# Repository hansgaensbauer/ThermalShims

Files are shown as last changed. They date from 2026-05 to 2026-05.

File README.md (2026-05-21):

# Thermal Shims

## Shim Demos

### Concentric Rings

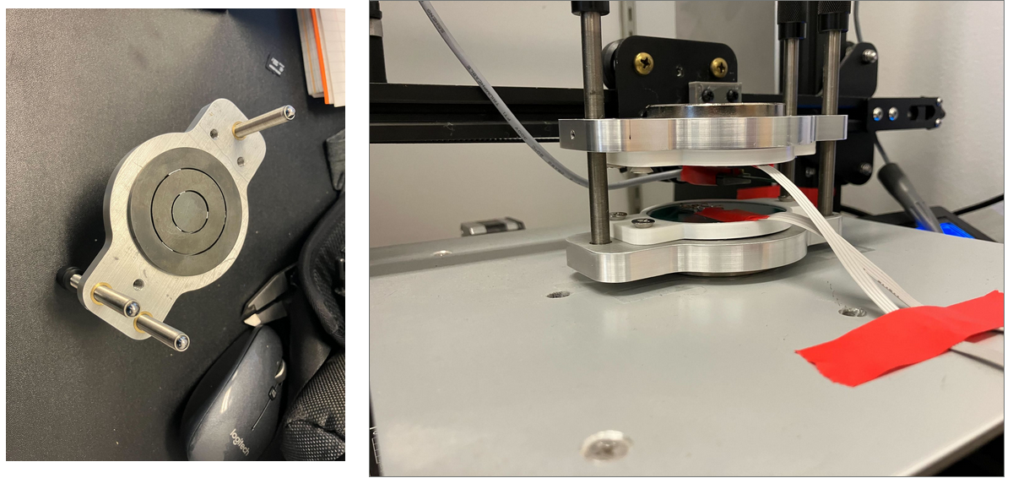
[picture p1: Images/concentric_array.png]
Concentric Ring Demo


This demonstration uses a 4mm ferrite plate cut to size on a waterjet. Each ring is connected to a PCB heater that is counterwound to prevent the development of magnetic fields from the heater current.

### 12x12 Array

This board demonstrates independent closed-loop control over the temperature of 144 ferrite elements. Each ferrite element has a temperature control unit cell attached on the backside of the PCB. This circuit uses two dual-MOSFETs to provide DRAM-like array access to the power setting and temperature readout for that element:

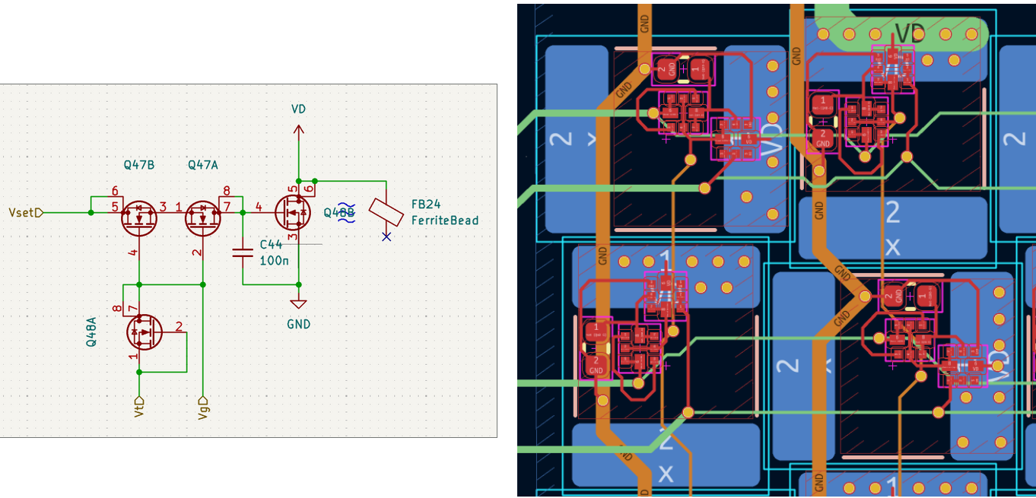
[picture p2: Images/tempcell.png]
A temperature control unit cell schematic and layout


These unit cells can then be connected to form a larger array of N elements, with only sqrt(N) control circuits/ADCs required:

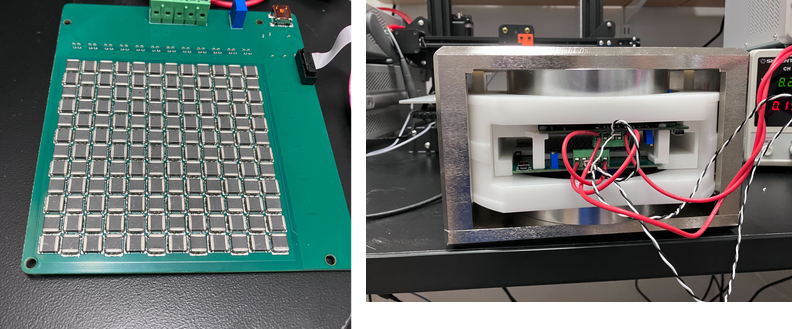
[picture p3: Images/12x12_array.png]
The shim arrays installed in a permanent magnet

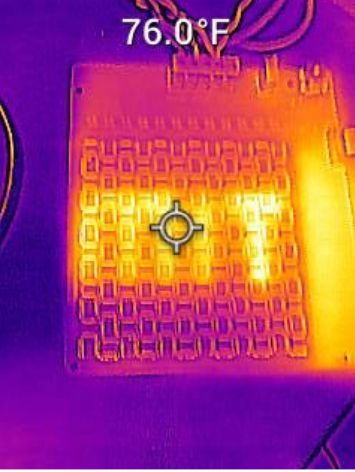
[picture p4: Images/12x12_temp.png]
A demonstration of the independent temperature control


The `12x12 Array` folder contains simulations of the control circuits showing the sequencing required to measure the temperature or set the cell power level. All of this circuitry is included on the PCB for the 12x12 array demo.

### Hub & Spoke NdFeB Magnet Shimming

This board provides temperature control and sensing for 32 NdFeB magnets in a hub & spoke magnet array. This can be used to prevent temperature drift between the magnets during a scan, or even to account for variations in the magnetization of the individual elements. 

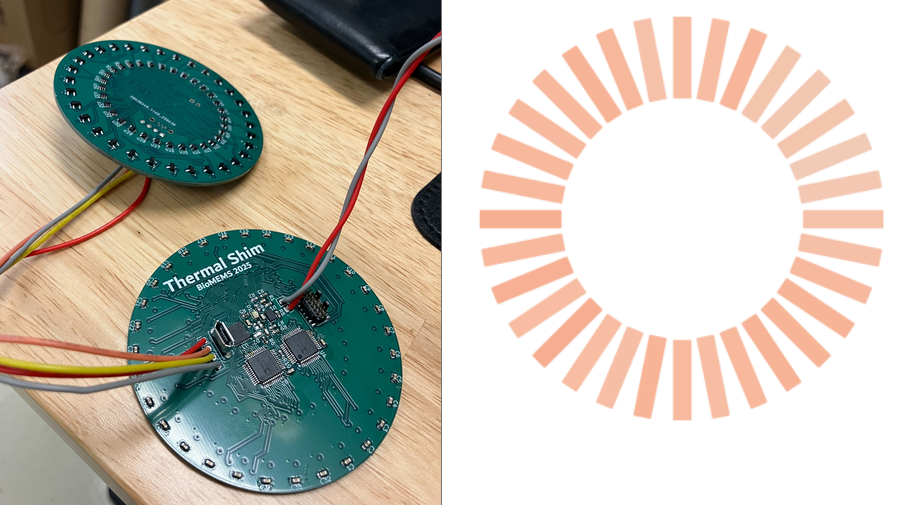
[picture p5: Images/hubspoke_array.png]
Hub and spoke magnet temperature control


## Simulations
The jupyter notebook in the Simulations folder includes code for simulating different arrangements of thermal shims with different temperatures using [FEMM](https://www.femm.info/). These simulations assume an arctangent B/H curve that is parameterized by a linear relationship between the saturation magnetization and the temperature:

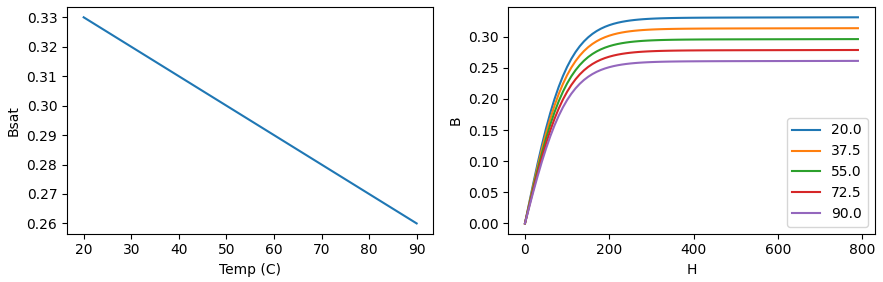
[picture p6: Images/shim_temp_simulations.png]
BH Curve simulations


To run a simulation with a certain material and temperature, the code creates a custom material based on the calculated BH curve in FEMM. To sweep the temperature, the same simulation is run with different materials.

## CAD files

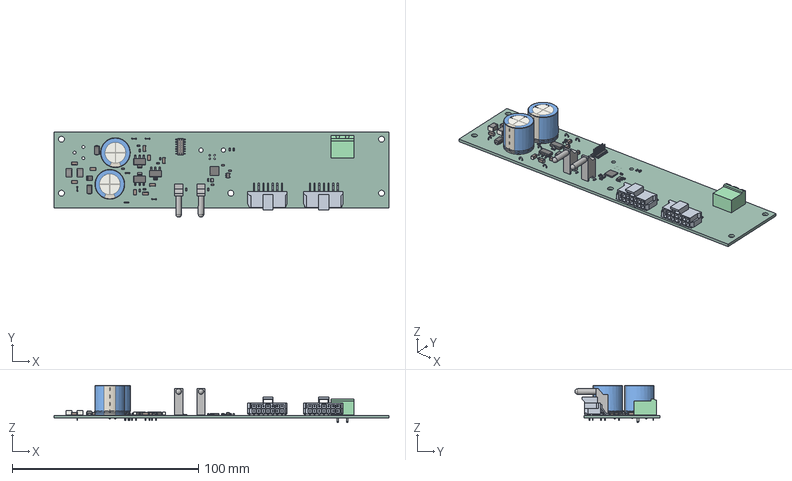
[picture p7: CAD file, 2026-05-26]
Flow Shims/hardware/controller/controller.step
180.0 x 45.9 x 20.0 mm
C_1206_3216Metric x 9
CP_Radial_D16.0mm_P7.50mm x 2
TestPoint_Bridge_Pitch2.0mm_Drill0.7mm x 6
SLP3-500-450-R x 2
C_0603_1608Metric x 5
L_1812_4532Metric x 2
R_0603_1608Metric x 10
D_SMA x 2
Crystal_SMD_2016-4Pin_2.0x1.6mm
LED_0603_1608Metric x 2
SOT-223 x 3
Fuse_1210_3225Metric
SOT-23-5
QFN-32-1EP_5x5mm_P0.5mm_EP3.45x3.45mm
PinHeader_2x07_P1.27mm_Vertical_SMD
PhoenixContact_MSTBA_2,5_2-G-5,08_1x02_P5.08mm_Horizontal
controller_PCB

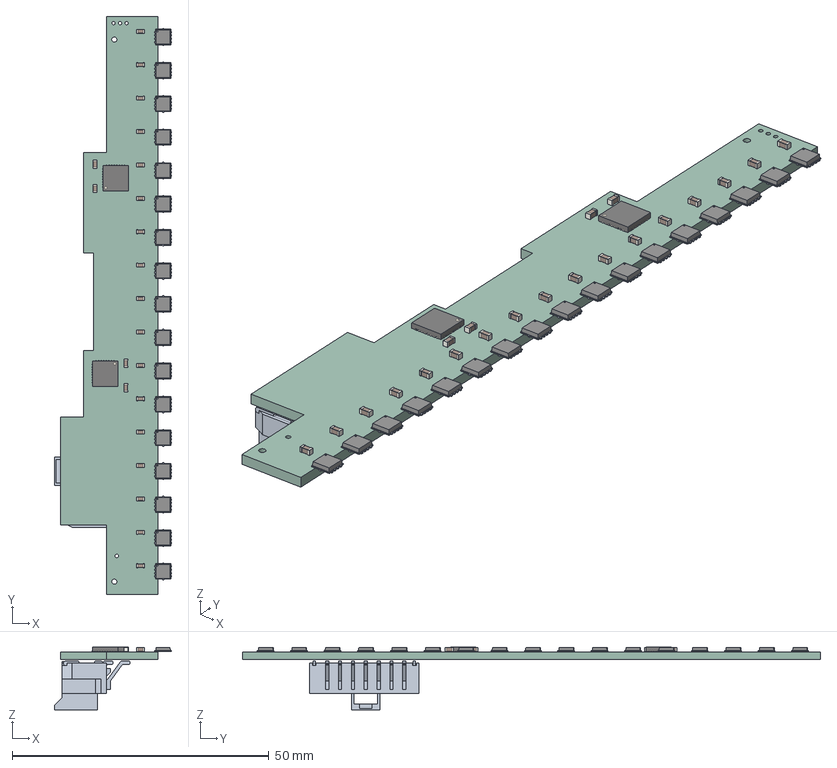
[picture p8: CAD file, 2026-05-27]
Flow Shims/hardware/heater17/heater17.step
22.8 x 112.5 x 12.3 mm
C_0603_1608Metric x 21
QFN-32-1EP_5x5mm_P0.5mm_EP3.3x3.3mm x 2
NVTFS5116PLTAG x 17
heater_PCB

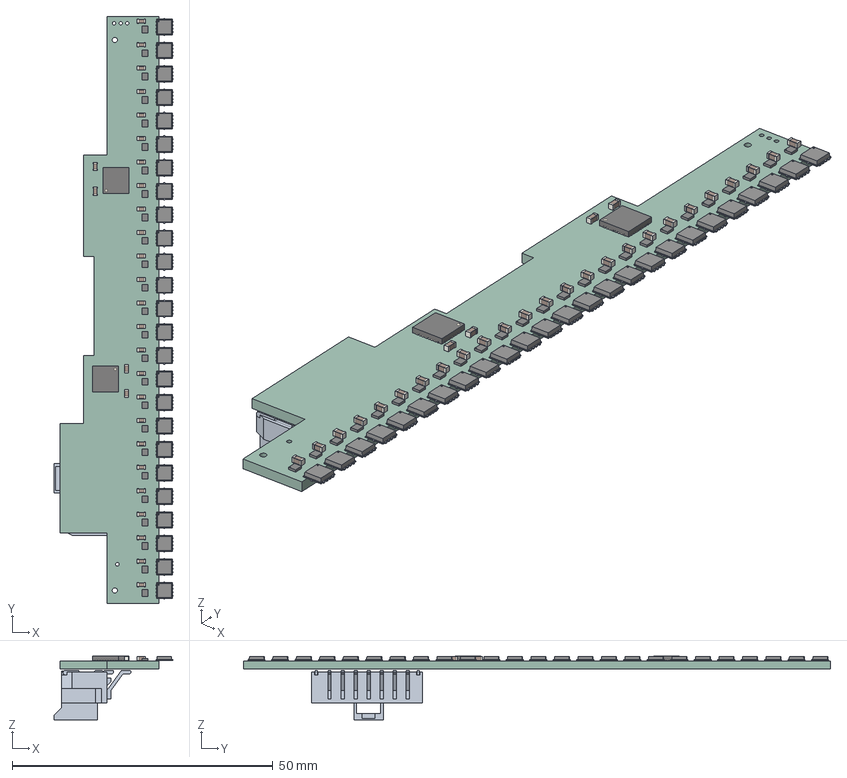
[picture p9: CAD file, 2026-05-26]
Flow Shims/hardware/heater25/heater.step
22.8 x 112.5 x 12.3 mm
NVTFS5116PLTAG x 25
C_0603_1608Metric x 29
QFN-32-1EP_5x5mm_P0.5mm_EP3.3x3.3mm x 2
DFN6_1_2X1_3_STM x 25
heater_PCB

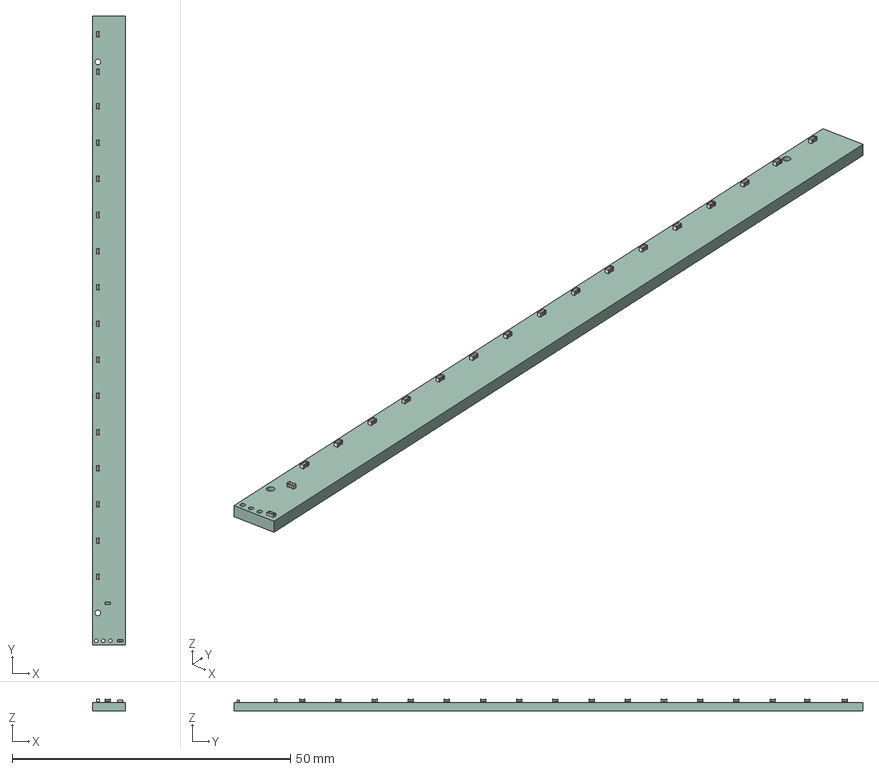
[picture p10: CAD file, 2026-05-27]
Flow Shims/hardware/temp_sensors17/temp_sensor17.step
6.00 x 113.0 x 2.09 mm
C_0402_1005Metric x 17
R_0402_1005Metric
temp_sensors_PCB

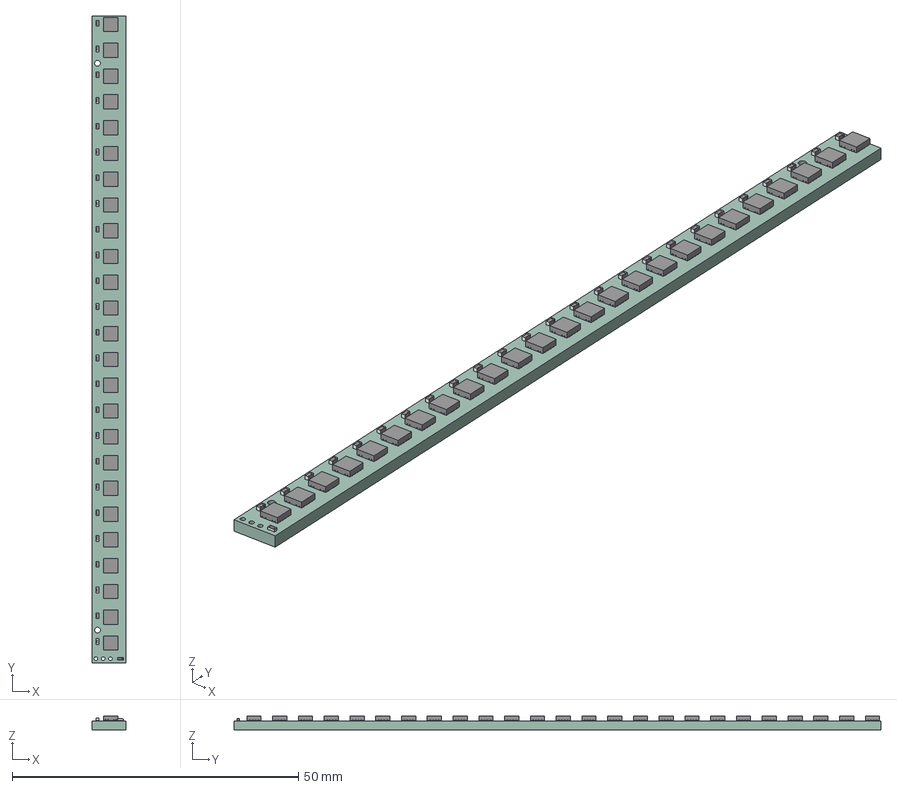
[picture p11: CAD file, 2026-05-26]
Flow Shims/hardware/temp_sensors25/temp_sensor.step
6.00 x 113.0 x 2.40 mm
C_0402_1005Metric x 25
BODY-SON x 25
FRAME-NGR0008C x 25
PIN1-ID x 25
R_0402_1005Metric
temp_sensors_PCB

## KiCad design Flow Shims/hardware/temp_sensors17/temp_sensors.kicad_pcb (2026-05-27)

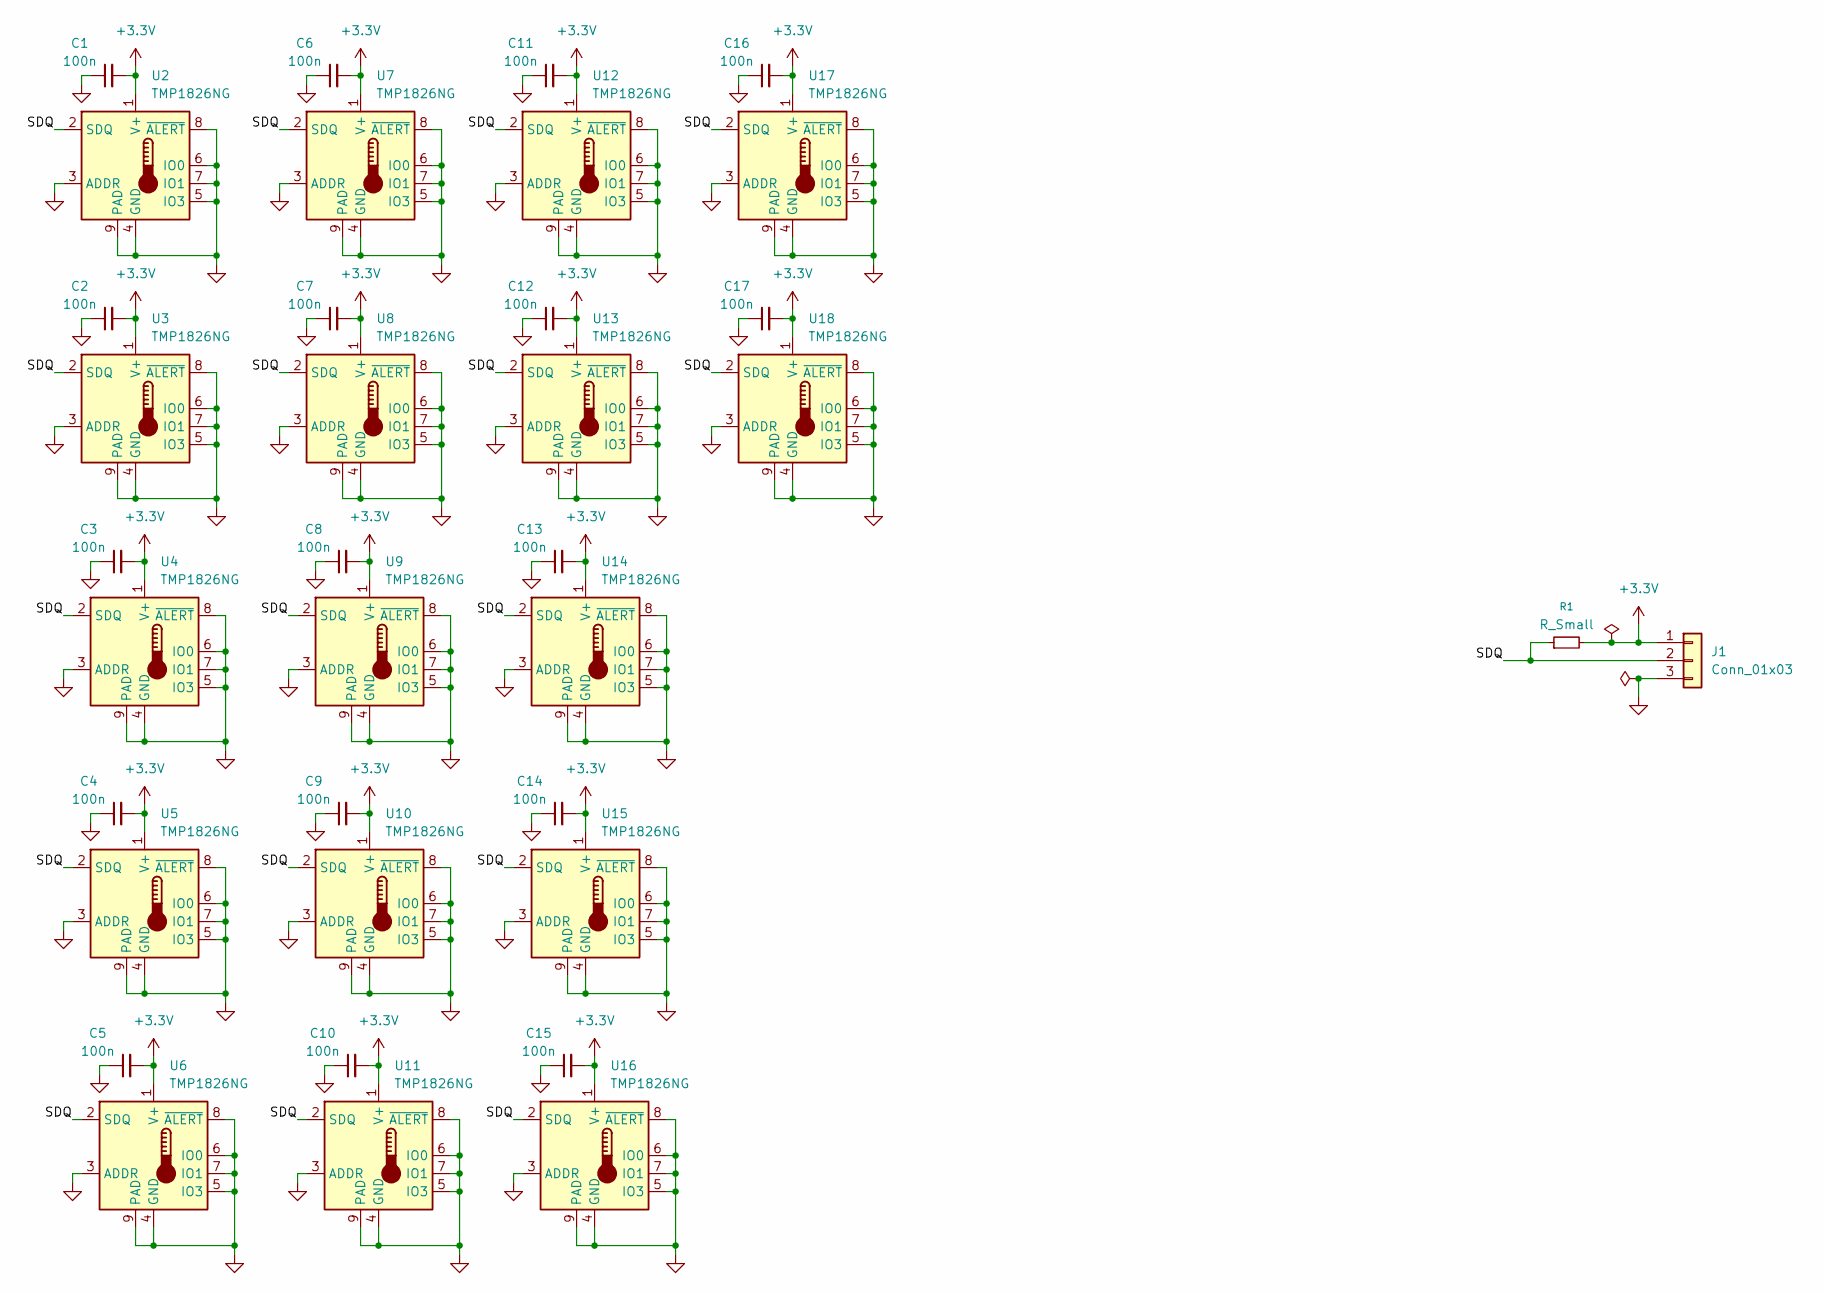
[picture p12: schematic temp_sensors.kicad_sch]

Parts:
C1, C2, C3, C4, C5, C6, C7, C8, C9, C10, C11, C12, C13, C14, C15, C16, C17: 100n; C_0402_1005Metric
J1: Conn_01x03; PinHeader_1x03_P1.27mm_Vertical
R1: R_Small; R_0402_1005Metric
U2, U3, U4, U5, U6, U7, U8, U9, U10, U11, U12, U13, U14, U15, U16, U17, U18: TMP1826NG; Sensirion_DFN-8-1EP_2.5x2.5mm_P0.5mm_EP1.1x1.7mm

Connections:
+3.3V: C1.2, C2.2, C3.2, C4.2, C5.2, C6.2, C7.2, C8.2, C9.2, C10.2, C11.2, C12.2, C13.2, C14.2, C15.2, C16.2, C17.2, J1.1, R1.2, U2.1 (V+), U3.1 (V+), U4.1 (V+), U5.1 (V+), U6.1 (V+), U7.1 (V+), U8.1 (V+), U9.1 (V+), U10.1 (V+), U11.1 (V+), U12.1 (V+), U13.1 (V+), U14.1 (V+), U15.1 (V+), U16.1 (V+), U17.1 (V+), U18.1 (V+)
/SDQ: J1.2, R1.1, U2.2 (SDQ), U3.2 (SDQ), U4.2 (SDQ), U5.2 (SDQ), U6.2 (SDQ), U7.2 (SDQ), U8.2 (SDQ), U9.2 (SDQ), U10.2 (SDQ), U11.2 (SDQ), U12.2 (SDQ), U13.2 (SDQ), U14.2 (SDQ), U15.2 (SDQ), U16.2 (SDQ), U17.2 (SDQ), U18.2 (SDQ)
GND: C1.1, C2.1, C3.1, C4.1, C5.1, C6.1, C7.1, C8.1, C9.1, C10.1, C11.1, C12.1, C13.1, C14.1, C15.1, C16.1, C17.1, J1.3, U2.3 (ADDR), U2.4 (GND), U2.5 (IO3), U2.6 (IO0), U2.7 (IO1), U2.8 (~ALERT), U2.9 (PAD), U3.3 (ADDR), U3.4 (GND), U3.5 (IO3), U3.6 (IO0), U3.7 (IO1), U3.8 (~ALERT), U3.9 (PAD), U4.3 (ADDR), U4.4 (GND), U4.5 (IO3), U4.6 (IO0), U4.7 (IO1), U4.8 (~ALERT), U4.9 (PAD), U5.3 (ADDR), U5.4 (GND), U5.5 (IO3), U5.6 (IO0), U5.7 (IO1), U5.8 (~ALERT), U5.9 (PAD), U6.3 (ADDR), U6.4 (GND), U6.5 (IO3), U6.6 (IO0), U6.7 (IO1), U6.8 (~ALERT), U6.9 (PAD), U7.3 (ADDR), U7.4 (GND), U7.5 (IO3), U7.6 (IO0), U7.7 (IO1), U7.8 (~ALERT), U7.9 (PAD), U8.3 (ADDR), U8.4 (GND), U8.5 (IO3), U8.6 (IO0), U8.7 (IO1), U8.8 (~ALERT), U8.9 (PAD), U9.3 (ADDR), U9.4 (GND), U9.5 (IO3), U9.6 (IO0), U9.7 (IO1), U9.8 (~ALERT), U9.9 (PAD), U10.3 (ADDR), U10.4 (GND), U10.5 (IO3), U10.6 (IO0), U10.7 (IO1), U10.8 (~ALERT), U10.9 (PAD), U11.3 (ADDR), U11.4 (GND), U11.5 (IO3), U11.6 (IO0), U11.7 (IO1), U11.8 (~ALERT), U11.9 (PAD), U12.3 (ADDR), U12.4 (GND), U12.5 (IO3), U12.6 (IO0), U12.7 (IO1), U12.8 (~ALERT), U12.9 (PAD), U13.3 (ADDR), U13.4 (GND), U13.5 (IO3), U13.6 (IO0), U13.7 (IO1), U13.8 (~ALERT), U13.9 (PAD), U14.3 (ADDR), U14.4 (GND), U14.5 (IO3), U14.6 (IO0), U14.7 (IO1), U14.8 (~ALERT), U14.9 (PAD), U15.3 (ADDR), U15.4 (GND), U15.5 (IO3), U15.6 (IO0), U15.7 (IO1), U15.8 (~ALERT), U15.9 (PAD), U16.3 (ADDR), U16.4 (GND), U16.5 (IO3), U16.6 (IO0), U16.7 (IO1), U16.8 (~ALERT), U16.9 (PAD), U17.3 (ADDR), U17.4 (GND), U17.5 (IO3), U17.6 (IO0), U17.7 (IO1), U17.8 (~ALERT), U17.9 (PAD), U18.3 (ADDR), U18.4 (GND), U18.5 (IO3), U18.6 (IO0), U18.7 (IO1), U18.8 (~ALERT), U18.9 (PAD)

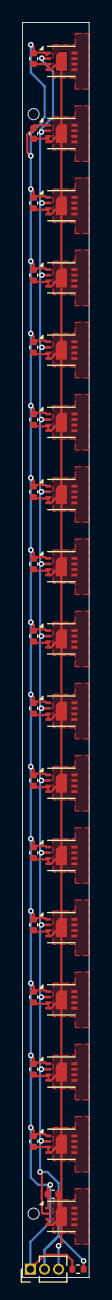
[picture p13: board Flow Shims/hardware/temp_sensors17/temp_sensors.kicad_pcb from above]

Board: 2 copper layers, 6.0 x 113.0 mm, 36 parts (0 on the bottom side), 3 nets.

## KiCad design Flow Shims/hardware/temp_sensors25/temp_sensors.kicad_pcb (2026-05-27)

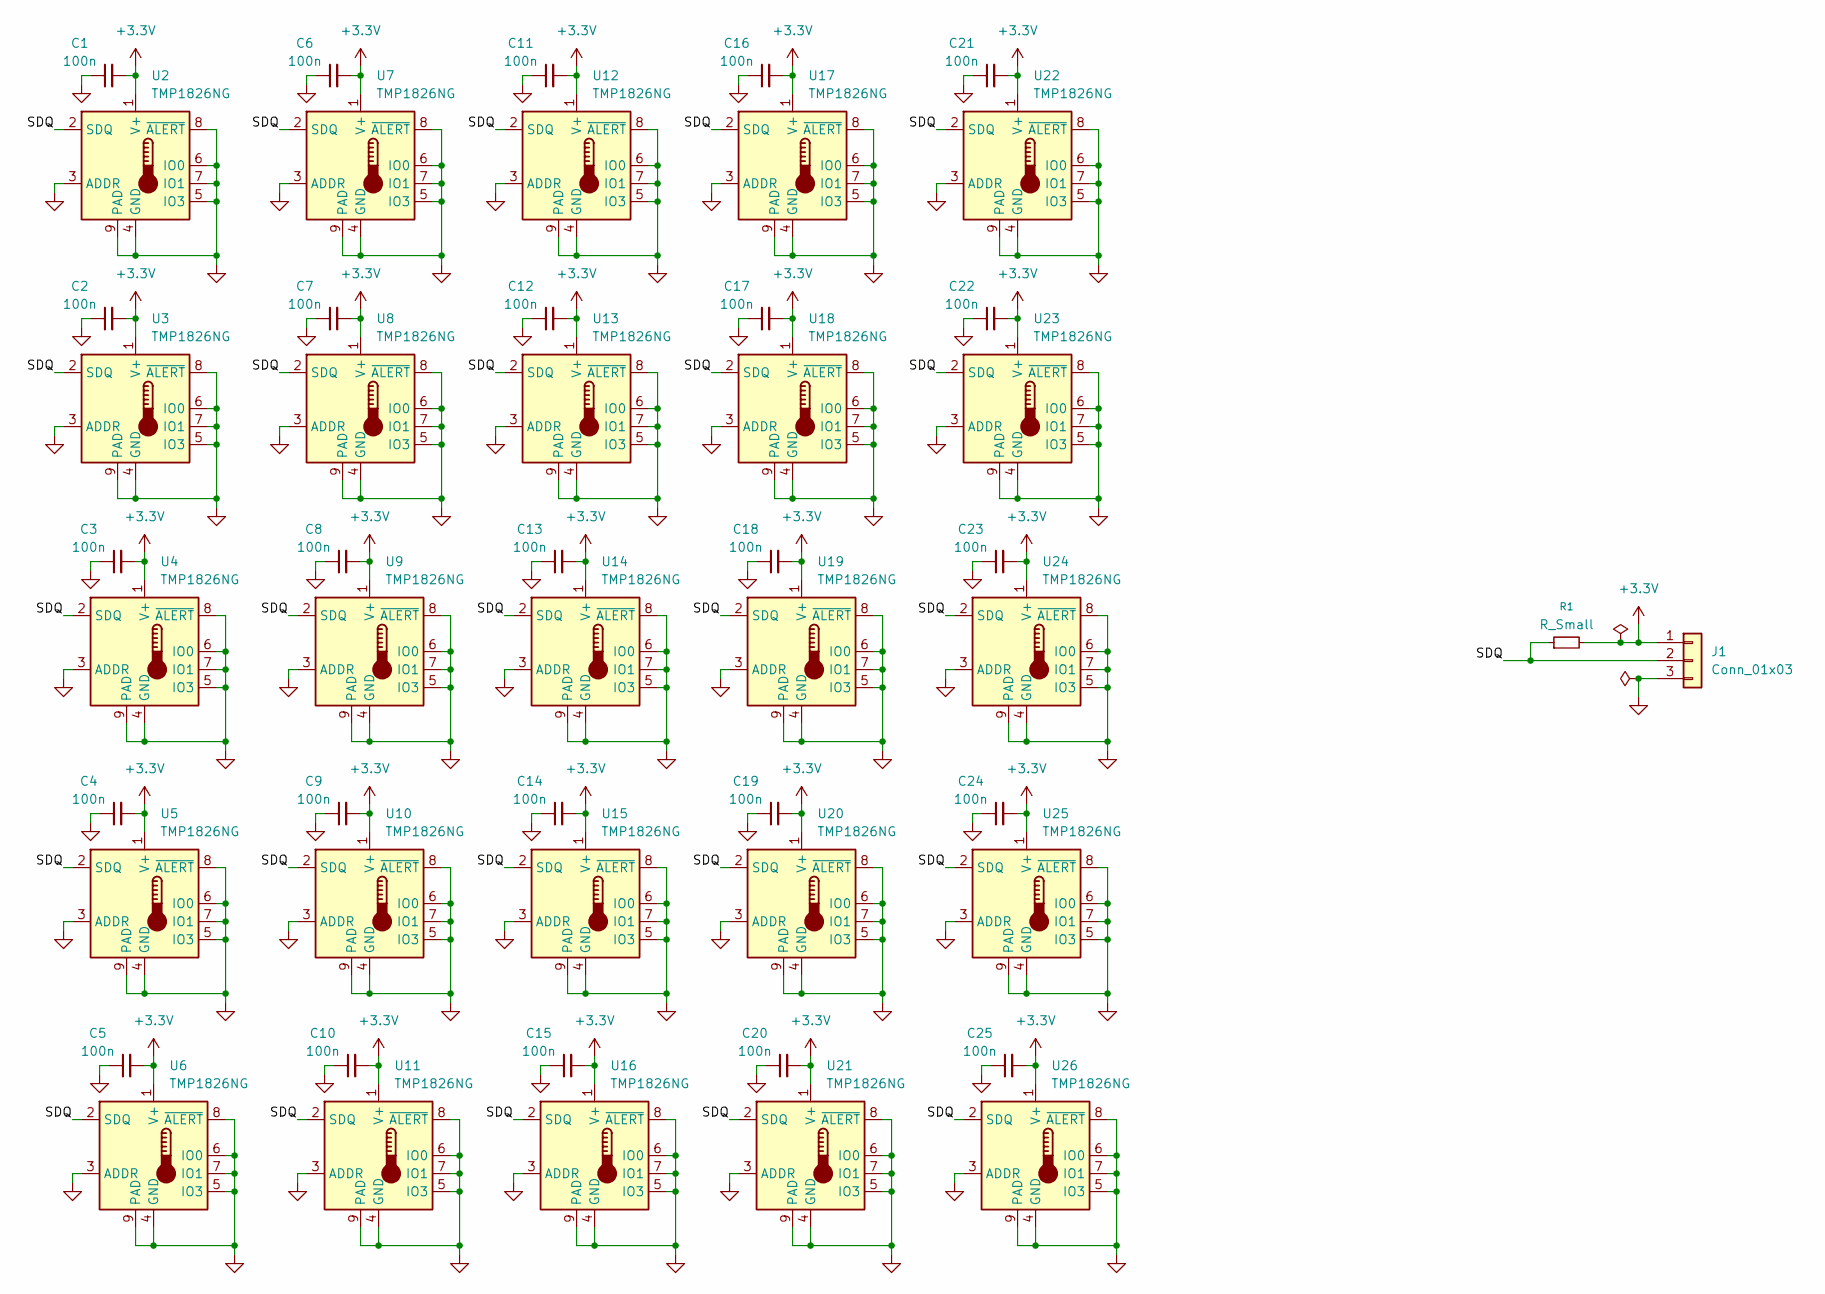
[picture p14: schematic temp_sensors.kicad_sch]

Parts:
C1, C2, C3, C4, C5, C6, C7, C8, C9, C10, C11, C12, C13, C14, C15, C16, C17, C18, C19, C20, C21, C22, C23, C24, C25: 100n; C_0402_1005Metric
J1: Conn_01x03; PinHeader_1x03_P1.27mm_Vertical
R1: R_Small; R_0402_1005Metric
U2, U3, U4, U5, U6, U7, U8, U9, U10, U11, U12, U13, U14, U15, U16, U17, U18, U19, U20, U21, U22, U23, U24, U25, U26: TMP1826NG; Sensirion_DFN-8-1EP_2.5x2.5mm_P0.5mm_EP1.1x1.7mm

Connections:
+3.3V: C1.2, C2.2, C3.2, C4.2, C5.2, C6.2, C7.2, C8.2, C9.2, C10.2, C11.2, C12.2, C13.2, C14.2, C15.2, C16.2, C17.2, C18.2, C19.2, C20.2, C21.2, C22.2, C23.2, C24.2, C25.2, J1.1, R1.2, U2.1 (V+), U3.1 (V+), U4.1 (V+), U5.1 (V+), U6.1 (V+), U7.1 (V+), U8.1 (V+), U9.1 (V+), U10.1 (V+), U11.1 (V+), U12.1 (V+), U13.1 (V+), U14.1 (V+), U15.1 (V+), U16.1 (V+), U17.1 (V+), U18.1 (V+), U19.1 (V+), U20.1 (V+), U21.1 (V+), U22.1 (V+), U23.1 (V+), U24.1 (V+), U25.1 (V+), U26.1 (V+)
/SDQ: J1.2, R1.1, U2.2 (SDQ), U3.2 (SDQ), U4.2 (SDQ), U5.2 (SDQ), U6.2 (SDQ), U7.2 (SDQ), U8.2 (SDQ), U9.2 (SDQ), U10.2 (SDQ), U11.2 (SDQ), U12.2 (SDQ), U13.2 (SDQ), U14.2 (SDQ), U15.2 (SDQ), U16.2 (SDQ), U17.2 (SDQ), U18.2 (SDQ), U19.2 (SDQ), U20.2 (SDQ), U21.2 (SDQ), U22.2 (SDQ), U23.2 (SDQ), U24.2 (SDQ), U25.2 (SDQ), U26.2 (SDQ)
GND: C1.1, C2.1, C3.1, C4.1, C5.1, C6.1, C7.1, C8.1, C9.1, C10.1, C11.1, C12.1, C13.1, C14.1, C15.1, C16.1, C17.1, C18.1, C19.1, C20.1, C21.1, C22.1, C23.1, C24.1, C25.1, J1.3, U2.3 (ADDR), U2.4 (GND), U2.5 (IO3), U2.6 (IO0), U2.7 (IO1), U2.8 (~ALERT), U2.9 (PAD), U3.3 (ADDR), U3.4 (GND), U3.5 (IO3), U3.6 (IO0), U3.7 (IO1), U3.8 (~ALERT), U3.9 (PAD), U4.3 (ADDR), U4.4 (GND), U4.5 (IO3), U4.6 (IO0), U4.7 (IO1), U4.8 (~ALERT), U4.9 (PAD), U5.3 (ADDR), U5.4 (GND), U5.5 (IO3), U5.6 (IO0), U5.7 (IO1), U5.8 (~ALERT), U5.9 (PAD), U6.3 (ADDR), U6.4 (GND), U6.5 (IO3), U6.6 (IO0), U6.7 (IO1), U6.8 (~ALERT), U6.9 (PAD), U7.3 (ADDR), U7.4 (GND), U7.5 (IO3), U7.6 (IO0), U7.7 (IO1), U7.8 (~ALERT), U7.9 (PAD), U8.3 (ADDR), U8.4 (GND), U8.5 (IO3), U8.6 (IO0), U8.7 (IO1), U8.8 (~ALERT), U8.9 (PAD), U9.3 (ADDR), U9.4 (GND), U9.5 (IO3), U9.6 (IO0), U9.7 (IO1), U9.8 (~ALERT), U9.9 (PAD), U10.3 (ADDR), U10.4 (GND), U10.5 (IO3), U10.6 (IO0), U10.7 (IO1), U10.8 (~ALERT), U10.9 (PAD), U11.3 (ADDR), U11.4 (GND), U11.5 (IO3), U11.6 (IO0), U11.7 (IO1), U11.8 (~ALERT), U11.9 (PAD), U12.3 (ADDR), U12.4 (GND), U12.5 (IO3), U12.6 (IO0), U12.7 (IO1), U12.8 (~ALERT), U12.9 (PAD), U13.3 (ADDR), U13.4 (GND), U13.5 (IO3), U13.6 (IO0), U13.7 (IO1), U13.8 (~ALERT), U13.9 (PAD), U14.3 (ADDR), U14.4 (GND), U14.5 (IO3), U14.6 (IO0), U14.7 (IO1), U14.8 (~ALERT), U14.9 (PAD), U15.3 (ADDR), U15.4 (GND), U15.5 (IO3), U15.6 (IO0), U15.7 (IO1), U15.8 (~ALERT), U15.9 (PAD), U16.3 (ADDR), U16.4 (GND), U16.5 (IO3), U16.6 (IO0), U16.7 (IO1), U16.8 (~ALERT), U16.9 (PAD), U17.3 (ADDR), U17.4 (GND), U17.5 (IO3), U17.6 (IO0), U17.7 (IO1), U17.8 (~ALERT), U17.9 (PAD), U18.3 (ADDR), U18.4 (GND), U18.5 (IO3), U18.6 (IO0), U18.7 (IO1), U18.8 (~ALERT), U18.9 (PAD), U19.3 (ADDR), U19.4 (GND), U19.5 (IO3), U19.6 (IO0), U19.7 (IO1), U19.8 (~ALERT), U19.9 (PAD), U20.3 (ADDR), U20.4 (GND), U20.5 (IO3), U20.6 (IO0), U20.7 (IO1), U20.8 (~ALERT), U20.9 (PAD), U21.3 (ADDR), U21.4 (GND), U21.5 (IO3), U21.6 (IO0), U21.7 (IO1), U21.8 (~ALERT), U21.9 (PAD), U22.3 (ADDR), U22.4 (GND), U22.5 (IO3), U22.6 (IO0), U22.7 (IO1), U22.8 (~ALERT), U22.9 (PAD), U23.3 (ADDR), U23.4 (GND), U23.5 (IO3), U23.6 (IO0), U23.7 (IO1), U23.8 (~ALERT), U23.9 (PAD), U24.3 (ADDR), U24.4 (GND), U24.5 (IO3), U24.6 (IO0), U24.7 (IO1), U24.8 (~ALERT), U24.9 (PAD), U25.3 (ADDR), U25.4 (GND), U25.5 (IO3), U25.6 (IO0), U25.7 (IO1), U25.8 (~ALERT), U25.9 (PAD), U26.3 (ADDR), U26.4 (GND), U26.5 (IO3), U26.6 (IO0), U26.7 (IO1), U26.8 (~ALERT), U26.9 (PAD)

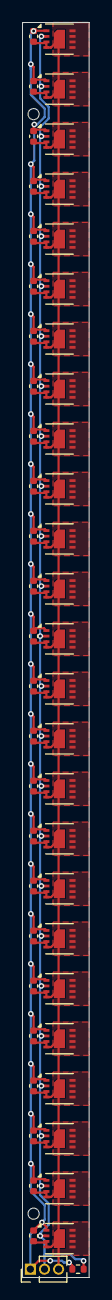
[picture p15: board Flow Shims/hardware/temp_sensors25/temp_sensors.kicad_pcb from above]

Board: 2 copper layers, 6.0 x 113.0 mm, 52 parts (0 on the bottom side), 3 nets.

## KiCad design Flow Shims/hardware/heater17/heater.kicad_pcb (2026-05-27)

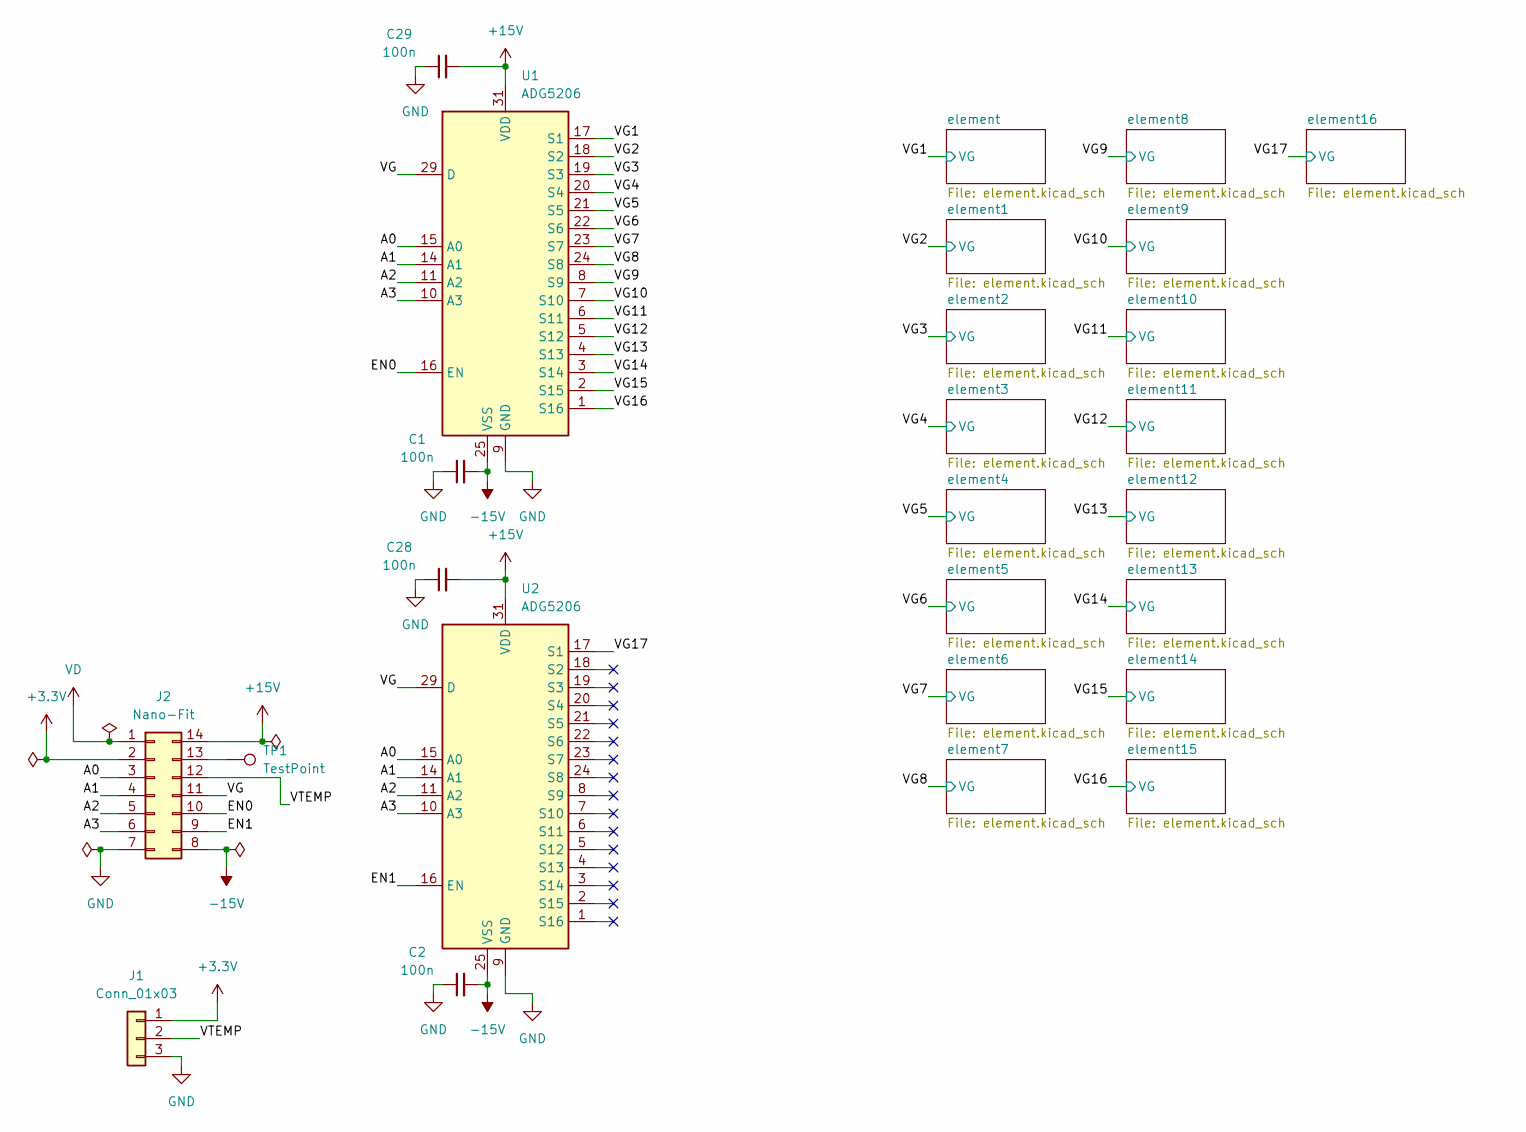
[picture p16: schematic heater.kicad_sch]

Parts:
C1, C2, C28, C29: 100n; C_0603_1608Metric
J1: Conn_01x03; PinHeader_1x03_P1.27mm_Vertical
J2: Nano-Fit; CONN_SD-105405-001_14_MOL
TP1: TestPoint; TestPoint_THTPad_D1.5mm_Drill0.7mm
U1, U2: ADG5206; QFN-32-1EP_5x5mm_P0.5mm_EP3.6x3.6mm

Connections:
+3.3V: J1.1, J2.2; also elsewhere on the board
+15V: C28.2, C29.2, J2.14, U1.31 (VDD), U2.31 (VDD)
-15V: C1.2, C2.2, J2.8, U1.25 (VSS), U1.33 (PAD), U2.25 (VSS), U2.33 (PAD)
/A0: J2.3, U1.15 (A0), U2.15 (A0)
/A1: J2.4, U1.14 (A1), U2.14 (A1)
/A2: J2.5, U1.11 (A2), U2.11 (A2)
/A3: J2.6, U1.10 (A3), U2.10 (A3)
/EN0: J2.10, U1.16 (EN)
/EN1: J2.9, U2.16 (EN)
/VG: J2.11, U1.29 (D), U2.29 (D)
/VG1: U1.17 (S1); also elsewhere on the board
/VG2: U1.18 (S2); also elsewhere on the board
/VG3: U1.19 (S3); also elsewhere on the board
/VG4: U1.20 (S4); also elsewhere on the board
/VG5: U1.21 (S5); also elsewhere on the board
/VG6: U1.22 (S6); also elsewhere on the board
/VG7: U1.23 (S7); also elsewhere on the board
/VG8: U1.24 (S8); also elsewhere on the board
/VG9: U1.8 (S9); also elsewhere on the board
/VG10: U1.7 (S10); also elsewhere on the board
/VG11: U1.6 (S11); also elsewhere on the board
/VG12: U1.5 (S12); also elsewhere on the board
/VG13: U1.4 (S13); also elsewhere on the board
/VG14: U1.3 (S14); also elsewhere on the board
/VG15: U1.2 (S15); also elsewhere on the board
/VG16: U1.1 (S16); also elsewhere on the board
/VG17: U2.17 (S1); also elsewhere on the board
/VTEMP: J1.2, J2.12
GND: C1.1, C2.1, C28.1, C29.1, J1.3, J2.7, U1.9 (GND), U2.9 (GND); also elsewhere on the board
unnamed: J2.13, TP1.1 (1_1)
VD: J2.1; also elsewhere on the board

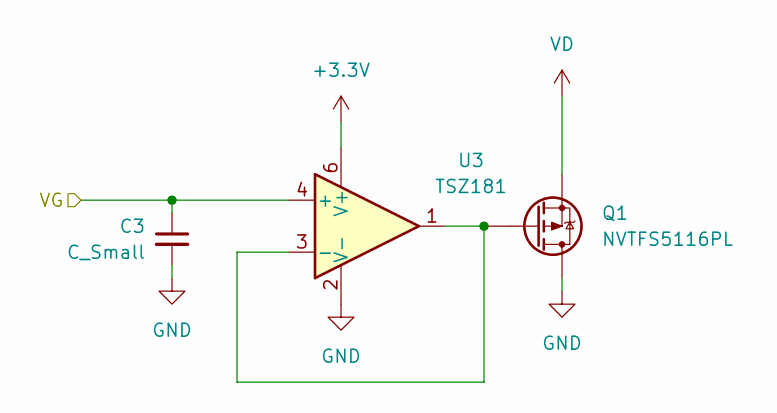
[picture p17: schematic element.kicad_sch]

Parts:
C3: C_Small; C_0603_1608Metric
Q1: NVTFS5116PL; WDFN8_511AB_ONS_OSI
U3: TSZ181; DFN-6_1.3x1.2mm_P0.4mm

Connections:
+3.3V: U3.6 (V+); also elsewhere on the board
/VG1: C3.1, U3.4 (+); also elsewhere on the board
GND: C3.2, Q1.5, Q1.6, Q1.7, Q1.8, U3.2 (V-); also elsewhere on the board
unnamed: Q1.4, U3.1, U3.3 (-)
VD: Q1.1, Q1.2, Q1.3; also elsewhere on the board

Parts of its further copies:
C4, C5, C6, C7, C8, C9, C10, C11, C12, C13, C14, C15, C16, C17, C18, C19: C_Small; C_0603_1608Metric
Q2, Q3, Q4, Q5, Q6, Q7, Q8, Q9, Q10, Q11, Q12, Q13, Q14, Q15, Q16, Q17: NVTFS5116PL; WDFN8_511AB_ONS_OSI
U4, U5, U6, U7, U8, U9, U10, U11, U12, U13, U14, U15, U16, U17, U18, U19: TSZ181; DFN-6_1.3x1.2mm_P0.4mm

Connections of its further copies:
+3.3V: U4.6 (V+), U5.6 (V+), U6.6 (V+), U7.6 (V+), U8.6 (V+), U9.6 (V+), U10.6 (V+), U11.6 (V+), U12.6 (V+), U13.6 (V+), U14.6 (V+), U15.6 (V+), U16.6 (V+), U17.6 (V+), U18.6 (V+), U19.6 (V+); also elsewhere on the board
/VG2: C4.1, U4.4 (+); also elsewhere on the board
/VG3: C5.1, U5.4 (+); also elsewhere on the board
/VG4: C6.1, U6.4 (+); also elsewhere on the board
/VG5: C7.1, U7.4 (+); also elsewhere on the board
/VG6: C8.1, U8.4 (+); also elsewhere on the board
/VG7: C9.1, U9.4 (+); also elsewhere on the board
/VG8: C10.1, U10.4 (+); also elsewhere on the board
/VG9: C11.1, U11.4 (+); also elsewhere on the board
/VG10: C12.1, U12.4 (+); also elsewhere on the board
/VG11: C13.1, U13.4 (+); also elsewhere on the board
/VG12: C14.1, U14.4 (+); also elsewhere on the board
/VG13: C15.1, U15.4 (+); also elsewhere on the board
/VG14: C16.1, U16.4 (+); also elsewhere on the board
/VG15: C17.1, U17.4 (+); also elsewhere on the board
/VG16: C18.1, U18.4 (+); also elsewhere on the board
/VG17: C19.1, U19.4 (+); also elsewhere on the board
GND: C4.2, C5.2, C6.2, C7.2, C8.2, C9.2, C10.2, C11.2, C12.2, C13.2, C14.2, C15.2, C16.2, C17.2, C18.2, C19.2, Q2.5, Q2.6, Q2.7, Q2.8, Q3.5, Q3.6, Q3.7, Q3.8, Q4.5, Q4.6, Q4.7, Q4.8, Q5.5, Q5.6, Q5.7, Q5.8, Q6.5, Q6.6, Q6.7, Q6.8, Q7.5, Q7.6, Q7.7, Q7.8, Q8.5, Q8.6, Q8.7, Q8.8, Q9.5, Q9.6, Q9.7, Q9.8, Q10.5, Q10.6, Q10.7, Q10.8, Q11.5, Q11.6, Q11.7, Q11.8, Q12.5, Q12.6, Q12.7, Q12.8, Q13.5, Q13.6, Q13.7, Q13.8, Q14.5, Q14.6, Q14.7, Q14.8, Q15.5, Q15.6, Q15.7, Q15.8, Q16.5, Q16.6, Q16.7, Q16.8, Q17.5, Q17.6, Q17.7, Q17.8, U4.2 (V-), U5.2 (V-), U6.2 (V-), U7.2 (V-), U8.2 (V-), U9.2 (V-), U10.2 (V-), U11.2 (V-), U12.2 (V-), U13.2 (V-), U14.2 (V-), U15.2 (V-), U16.2 (V-), U17.2 (V-), U18.2 (V-), U19.2 (V-); also elsewhere on the board
unnamed: Q2.4, U4.1, U4.3 (-)
unnamed: Q3.4, U5.1, U5.3 (-)
unnamed: Q4.4, U6.1, U6.3 (-)
unnamed: Q5.4, U7.1, U7.3 (-)
unnamed: Q6.4, U8.1, U8.3 (-)
unnamed: Q7.4, U9.1, U9.3 (-)
unnamed: Q8.4, U10.1, U10.3 (-)
unnamed: Q9.4, U11.1, U11.3 (-)
unnamed: Q10.4, U12.1, U12.3 (-)
unnamed: Q11.4, U13.1, U13.3 (-)
unnamed: Q12.4, U14.1, U14.3 (-)
unnamed: Q13.4, U15.1, U15.3 (-)
unnamed: Q14.4, U16.1, U16.3 (-)
unnamed: Q15.4, U17.1, U17.3 (-)
unnamed: Q16.4, U18.1, U18.3 (-)
unnamed: Q17.4, U19.1, U19.3 (-)
VD: Q2.1, Q2.2, Q2.3, Q3.1, Q3.2, Q3.3, Q4.1, Q4.2, Q4.3, Q5.1, Q5.2, Q5.3, Q6.1, Q6.2, Q6.3, Q7.1, Q7.2, Q7.3, Q8.1, Q8.2, Q8.3, Q9.1, Q9.2, Q9.3, Q10.1, Q10.2, Q10.3, Q11.1, Q11.2, Q11.3, Q12.1, Q12.2, Q12.3, Q13.1, Q13.2, Q13.3, Q14.1, Q14.2, Q14.3, Q15.1, Q15.2, Q15.3, Q16.1, Q16.2, Q16.3, Q17.1, Q17.2, Q17.3; also elsewhere on the board

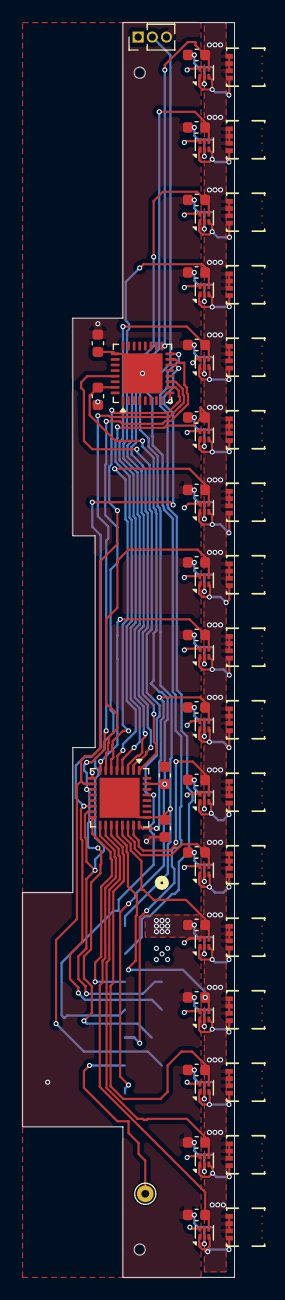
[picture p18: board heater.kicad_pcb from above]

Board: 4 copper layers, 19.0 x 112.5 mm, 60 parts (1 on the bottom side), 48 nets.

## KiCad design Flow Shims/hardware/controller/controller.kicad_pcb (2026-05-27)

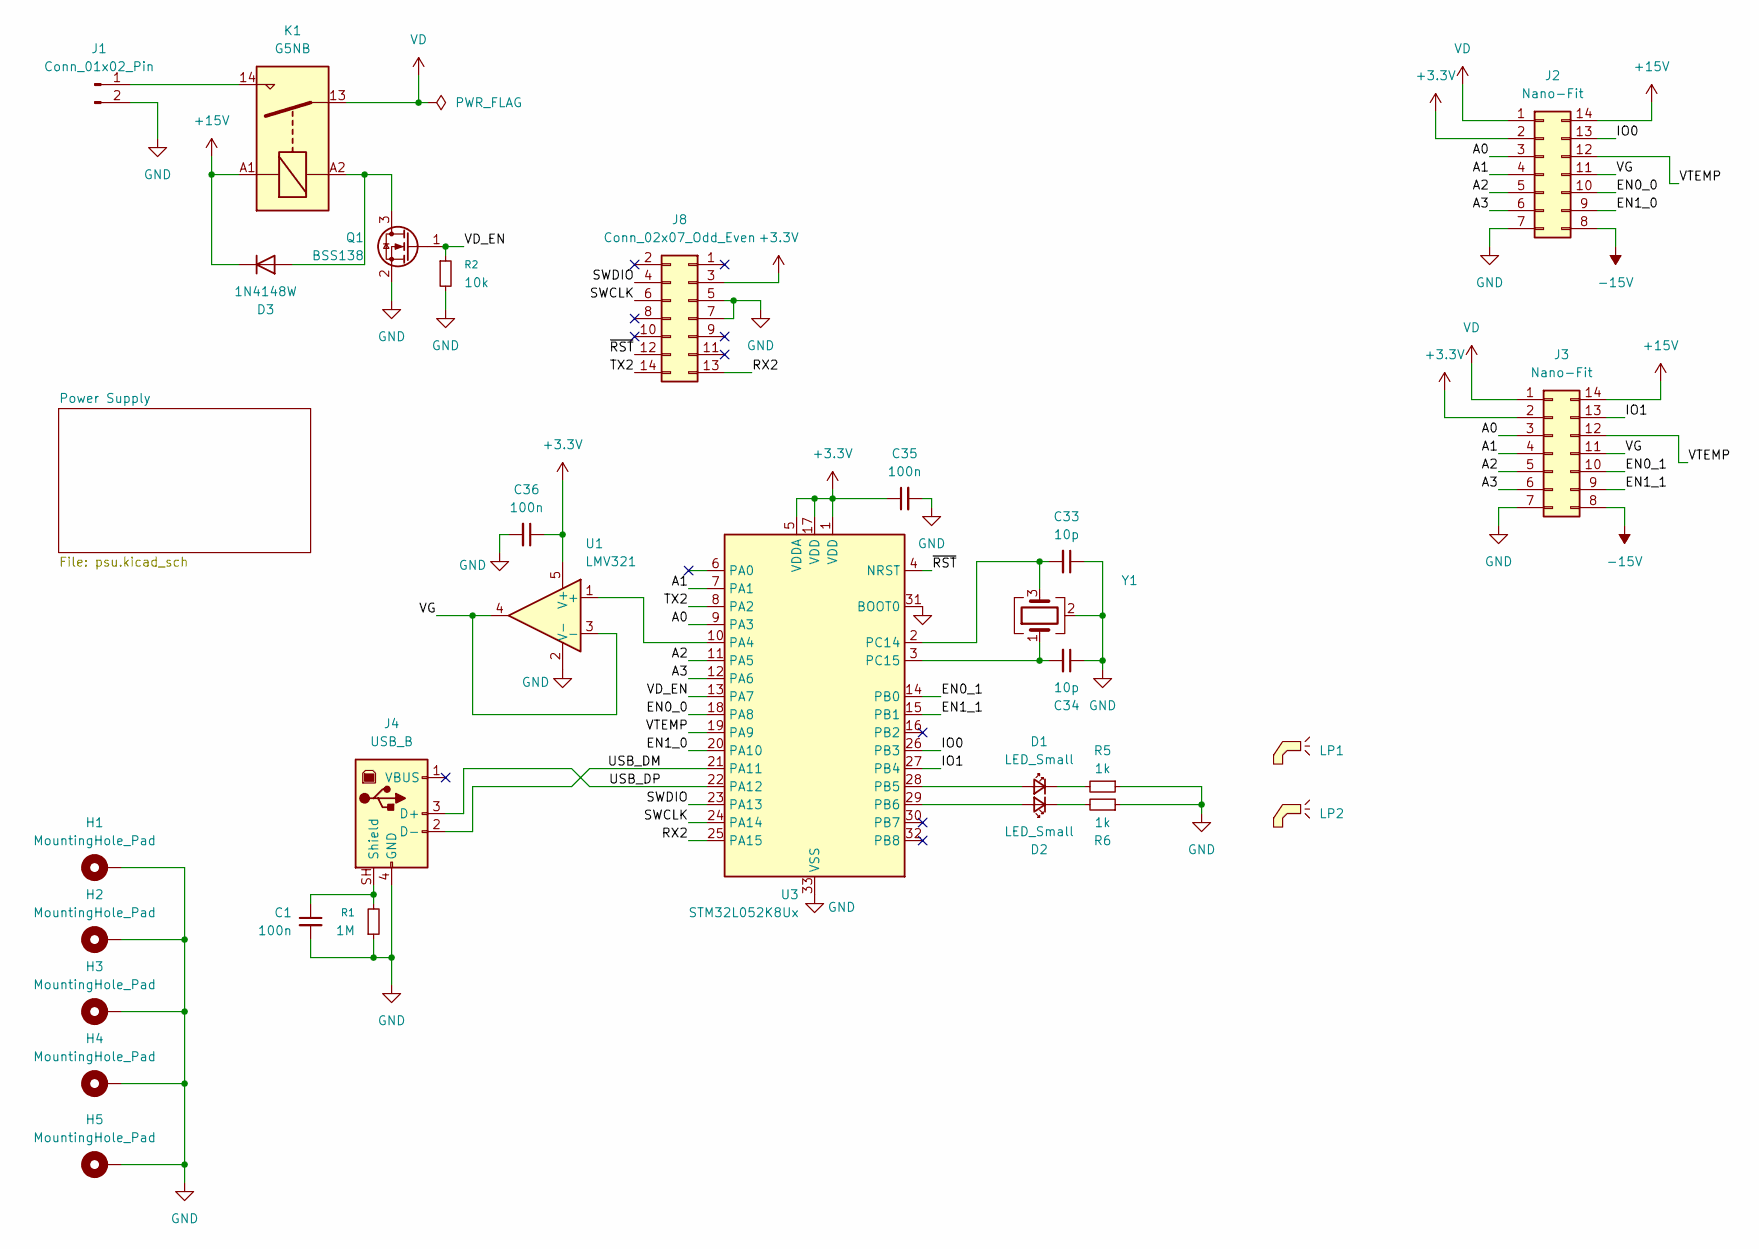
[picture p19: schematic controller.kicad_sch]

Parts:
C1, C35, C36: 100n; C_0603_1608Metric
C33, C34: 10p; C_0603_1608Metric
D1, D2: LED_Small; LED_0603_1608Metric
D3: 1N4148W; D_SOD-123
H1, H2, H3, H4, H5: MountingHole_Pad; MountingHole_3.2mm_M3_Pad
J1: Conn_01x02_Pin; PhoenixContact_MSTBA_2,5_2-G-5,08_1x02_P5.08mm_Horizontal
J2, J3: Nano-Fit; CONN_SD-105405-001_14_MOL
J4: USB_B; USB_B_OST_USB-B1HSxx_Horizontal
J8: Conn_02x07_Odd_Even; PinHeader_2x07_P1.27mm_Vertical_SMD
K1: G5NB; Relay_SPST_Omron_G5NB
LP1, LP2: SLP3-500-450-R
Q1: BSS138; SOT-23
R1: 1M; R_0603_1608Metric
R2: 10k
R5, R6: 1k; R_0603_1608Metric
U1: LMV321; SOT-23-5
U3: STM32L052K8Ux; QFN-32-1EP_5x5mm_P0.5mm_EP3.45x3.45mm
Y1: Crystal_GND24; Crystal_SMD_2016-4Pin_2.0x1.6mm

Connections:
+3.3V: C35.1, C36.1, J2.2, J3.2, J8.3, U1.5 (V+), U3.1 (VDD), U3.5 (VDDA), U3.17 (VDD); also elsewhere on the board
+15V: D3.1 (K), J2.14, J3.14, K1.A1; also elsewhere on the board
-15V: J2.8, J3.8; also elsewhere on the board
/A0: J2.3, J3.3, U3.9 (PA3)
/A1: J2.4, J3.4, U3.7 (PA1)
/A2: J2.5, J3.5, U3.11 (PA5)
/A3: J2.6, J3.6, U3.12 (PA6)
/EN0_0: J2.10, U3.18 (PA8)
/EN0_1: J3.10, U3.14 (PB0)
/EN1_0: J2.9, U3.20 (PA10)
/EN1_1: J3.9, U3.15 (PB1)
/IO0: J2.13, U3.26 (PB3)
/IO1: J3.13, U3.27 (PB4)
/RX2: J8.13, U3.25 (PA15)
/SWCLK: J8.6, U3.24 (PA14)
/SWDIO: J8.4, U3.23 (PA13)
/TX2: J8.14, U3.8 (PA2)
/USB_DM: J4.2 (D-), U3.21 (PA11)
/USB_DP: J4.3 (D+), U3.22 (PA12)
/VD_EN: Q1.1 (G), R2.1, U3.13 (PA7)
/VG: J2.11, J3.11, U1.3 (-), U1.4
/VTEMP: J2.12, J3.12, U3.19 (PA9)
/~RST: J8.12, U3.4 (NRST)
GND: C1.2, C33.1, C34.1, C35.2, C36.2, H1.1 (1_1), H2.1 (1_1), H3.1 (1_1), H4.1 (1_1), H5.1 (1_1), J1.2, J2.7, J3.7, J4.4 (GND), J8.5, J8.7, Q1.2 (S), R1.1, R2.2, R5.1, R6.1, U1.2 (V-), U3.31 (BOOT0), U3.33 (VSS), Y1.2 (G), Y1.4 (G); also elsewhere on the board
unnamed: D1.2 (A), U3.28 (PB5)
unnamed: D1.1 (K), R5.2
unnamed: D2.2 (A), U3.29 (PB6)
unnamed: D2.1 (K), R6.2
unnamed: D3.2 (A), K1.A2, Q1.3 (D)
unnamed: J1.1, K1.14
unnamed: C1.1, J4.SH (Shield), R1.2
unnamed: U1.1 (+), U3.10 (PA4)
unnamed: C33.2, U3.2 (PC14), Y1.3
unnamed: C34.2, U3.3 (PC15), Y1.1
VD: J2.1, J3.1, K1.13

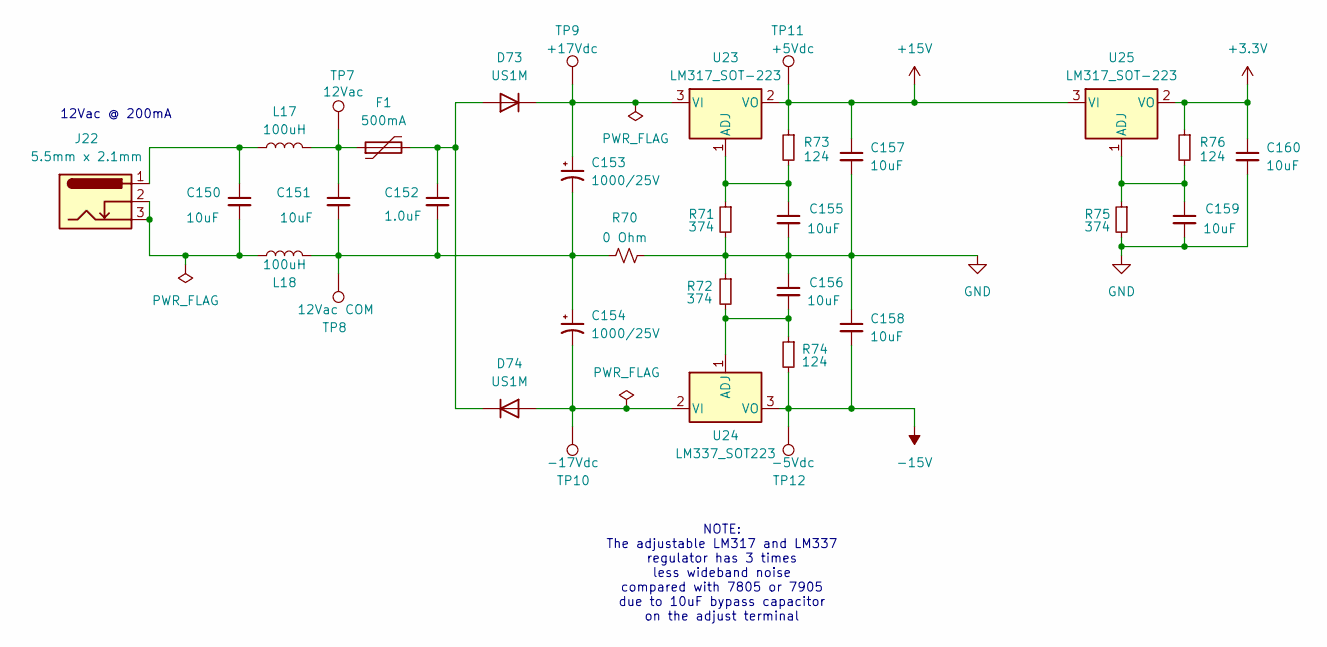
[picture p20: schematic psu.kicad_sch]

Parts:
C150, C151: 10uF; C_1206_3216Metric_Pad1.33x1.80mm_HandSolder
C152: 1.0uF; C_1206_3216Metric_Pad1.33x1.80mm_HandSolder
C153, C154: 1000/25V; CP_Radial_D16.0mm_P7.50mm
C155, C156, C157, C158, C159, C160: 10uF; C_1206_3216Metric
D73, D74: US1M; D_SMA
F1: 500mA; Fuse_1210_3225Metric_Pad1.42x2.65mm_HandSolder
J22: 5.5mm x 2.1mm; BarrelJack_CUI_PJ-102AH_Horizontal
L17, L18: 100uH; L_1812_4532Metric_Pad1.30x3.40mm_HandSolder
R70: 0 Ohm; R_0603_1608Metric
R71, R72, R75: 374; R_0603_1608Metric
R73, R74, R76: 124; R_0603_1608Metric
TP7: 12Vac; TestPoint_Bridge_Pitch2.0mm_Drill0.7mm
TP8: 12Vac COM; TestPoint_Bridge_Pitch2.0mm_Drill0.7mm
TP9: +17Vdc; TestPoint_Bridge_Pitch2.0mm_Drill0.7mm
TP10: -17Vdc; TestPoint_Bridge_Pitch2.0mm_Drill0.7mm
TP11: +5Vdc; TestPoint_Bridge_Pitch2.0mm_Drill0.7mm
TP12: -5Vdc; TestPoint_Bridge_Pitch2.0mm_Drill0.7mm
U23, U25: LM317_SOT-223; SOT-223-3_TabPin2
U24: LM337_SOT223; SOT-223-3_TabPin2

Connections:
+3.3V: C160.1, R76.1, U25.2 (VO); also elsewhere on the board
+15V: C157.1, R73.1, TP11.1 (1_1), U23.2 (VO), U25.3 (VI); also elsewhere on the board
-15V: C158.2, R74.2, TP12.1 (1_1), U24.3 (VO); also elsewhere on the board
GND: C155.2, C156.1, C157.2, C158.1, C159.2, C160.2, R70.2, R71.2, R72.1, R75.2; also elsewhere on the board
unnamed: C150.1, J22.1, L17.1
unnamed: C150.2, J22.2, J22.3, L18.1
unnamed: C151.1, F1.1, L17.2, TP7.1 (1_1)
unnamed: C151.2, C152.2, C153.2, C154.1, L18.2, R70.1, TP8.1 (1_1)
unnamed: C152.1, D73.2 (A), D74.1 (K), F1.2
unnamed: C153.1, D73.1 (K), TP9.1 (1_1), U23.3 (VI)
unnamed: C154.2, D74.2 (A), TP10.1 (1_1), U24.2 (VI)
unnamed: C155.1, R71.1, R73.2, U23.1 (ADJ)
unnamed: C156.2, R72.2, R74.1, U24.1 (ADJ)
unnamed: C159.1, R75.1, R76.2, U25.1 (ADJ)

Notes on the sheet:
12Vac @ 200mA
NOTE: The adjustable LM317 and LM337 regulator has 3 times less wideband noise compared with 7805 or 7905 due to 10uF bypass capacitor on the adjust terminal

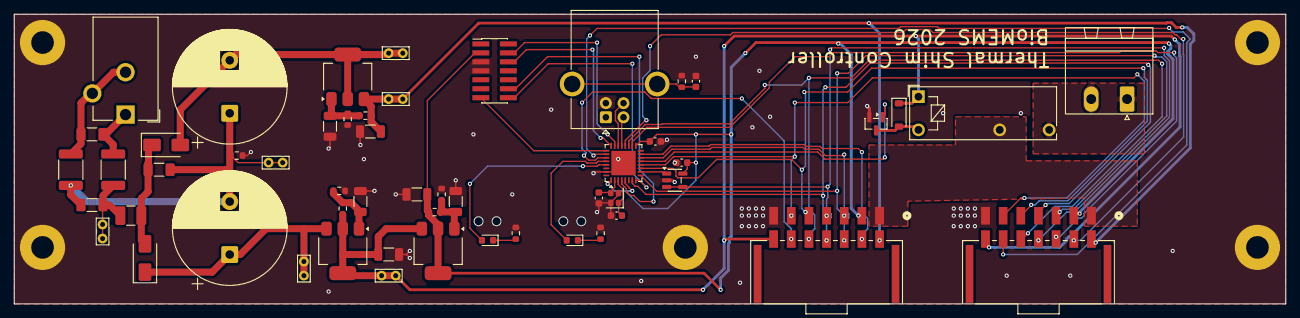
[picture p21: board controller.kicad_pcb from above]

Board: 2 copper layers, 180.0 x 41.0 mm, 61 parts (0 on the bottom side), 45 nets.

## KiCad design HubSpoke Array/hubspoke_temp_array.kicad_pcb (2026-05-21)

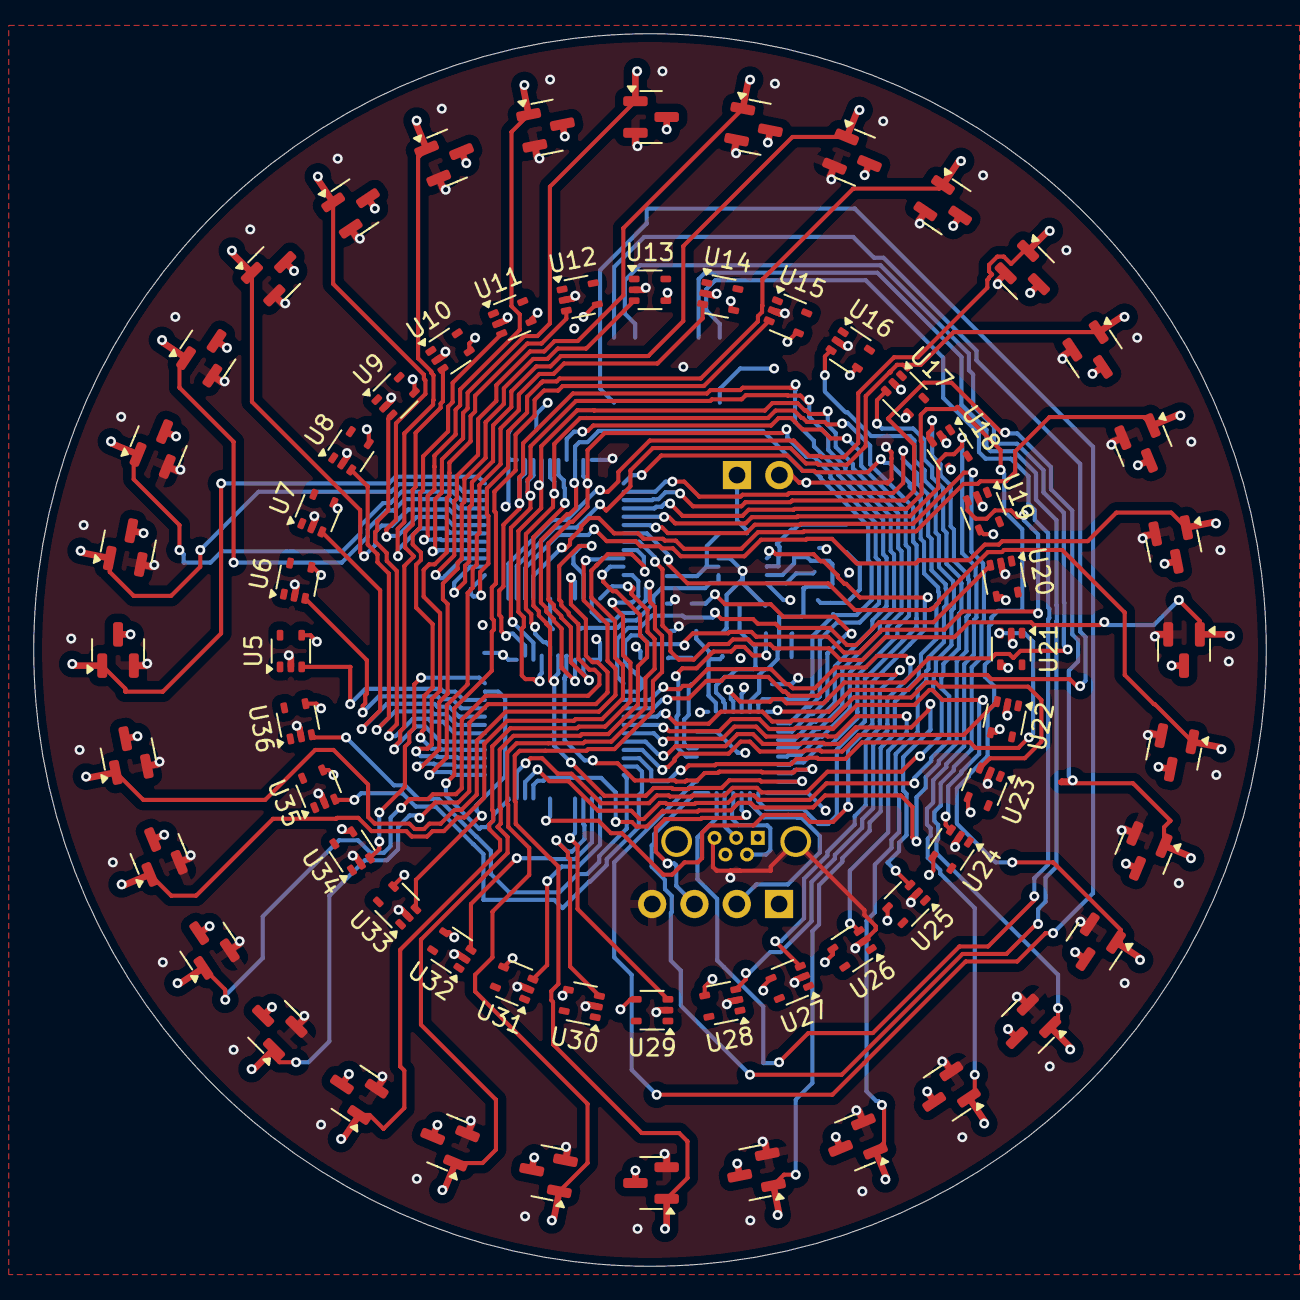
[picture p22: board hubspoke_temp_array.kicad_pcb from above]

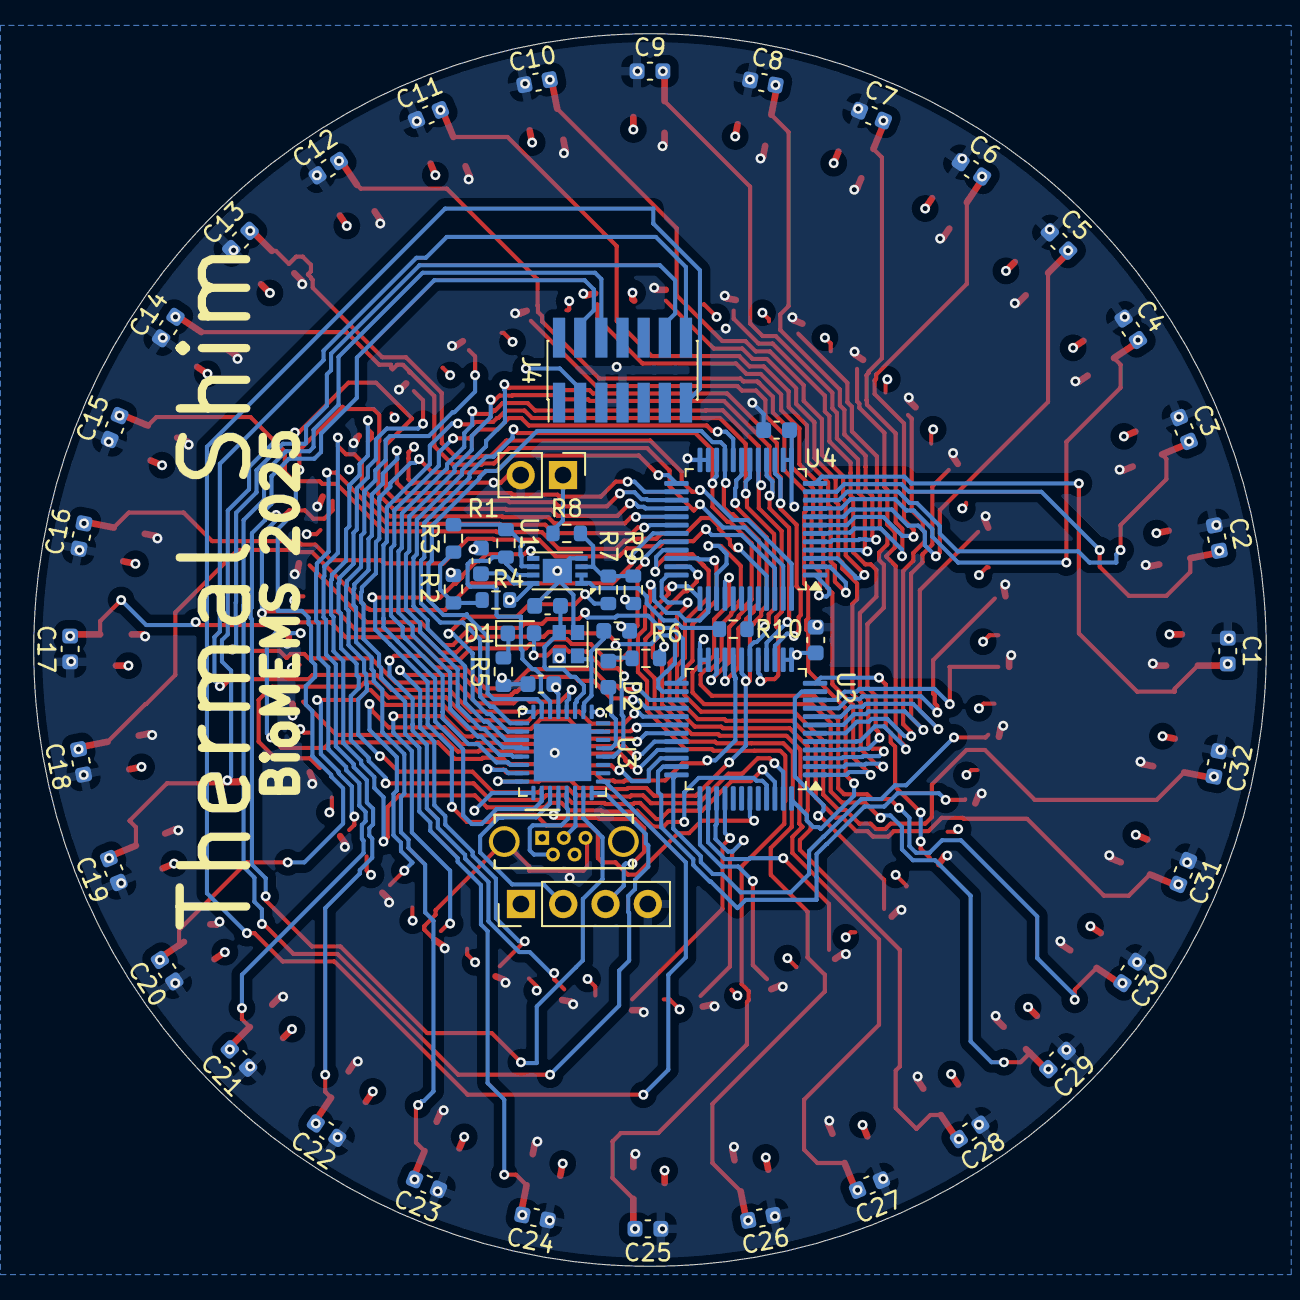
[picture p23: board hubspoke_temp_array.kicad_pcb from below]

Board: 4 copper layers, 74.0 x 74.0 mm, 123 parts (59 on the bottom side), 98 nets.

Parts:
C1, C2, C3, C4, C5, C6, C7, C8, C9, C10, C11, C12, C13, C14, C15, C16, C17, C18, C19, C20, C21, C22, C23, C24, C25, C26, C27, C28, C29, C30, C31, C32, C35, C36, C37, C38: 100n; C_0603_1608Metric
C33, C34: 10p; C_0603_1608Metric
D1, D2: LED_Small; LED_0603_1608Metric
J1: Conn_01x02_Pin; PinHeader_1x02_P2.54mm_Vertical
J2: Conn_01x04_Pin; PinHeader_1x04_P2.54mm_Vertical
J3: USB_B_Micro; USB_Micro-B_Wuerth_614105150721_Vertical_CircularHoles
J4: Conn_02x07_Odd_Even; PinHeader_2x07_P1.27mm_Vertical_SMD
Q1, Q2, Q3, Q4, Q5, Q6, Q7, Q8, Q9, Q10, Q11, Q12, Q13, Q14, Q15, Q16, Q17, Q18, Q19, Q20, Q21, Q22, Q23, Q24, Q25, Q26, Q27, Q28, Q29, Q30, Q31, Q32: BSS123NH6327XTSA1; SOT-23
R1, R2, R3, R4, R5, R6, R7, R8, R9, R10: R_Small; R_0603_1608Metric
U1: MCP6002-xMC; DFN-8-1EP_3x2mm_P0.5mm_EP1.75x1.45mm
U2, U4: ADG732; TQFP-48_7x7mm_P0.5mm
U3: STM32L052K8Ux; QFN-32-1EP_5x5mm_P0.5mm_EP3.45x3.45mm
U5, U6, U7, U8, U9, U10, U11, U12, U13, U14, U15, U16, U17, U18, U19, U20, U21, U22, U23, U24, U25, U26, U27, U28, U29, U30, U31, U32, U33, U34, U35, U36: MCP9700Ax-ELT; SOT-353_SC-70-5
Y1: Crystal_GND24; Crystal_SMD_2016-4Pin_2.0x1.6mm

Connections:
+3.3V: C35.1, C36.1, C37.1, C38.2, J1.1, J2.1, J4.3, Q1.3 (D), Q2.3 (D), Q3.3 (D), Q4.3 (D), Q5.3 (D), Q6.3 (D), Q7.3 (D), Q8.3 (D), Q9.3 (D), Q10.3 (D), Q11.3 (D), Q12.3 (D), Q13.3 (D), Q14.3 (D), Q15.3 (D), Q16.3 (D), Q17.3 (D), Q18.3 (D), Q19.3 (D), Q20.3 (D), Q21.3 (D), Q22.3 (D), Q23.3 (D), Q24.3 (D), Q25.3 (D), Q26.3 (D), Q27.3 (D), Q28.3 (D), Q29.3 (D), Q30.3 (D), Q31.3 (D), Q32.3 (D), R4.1, R8.2, U1.8 (V+), U2.13 (VDD), U2.14 (VDD), U3.1 (VDD), U3.5 (VDDA), U3.17 (VDD), U4.13 (VDD), U4.14 (VDD), U5.4 (V_{DD}), U6.4 (V_{DD}), U7.4 (V_{DD}), U8.4 (V_{DD}), U9.4 (V_{DD}), U10.4 (V_{DD}), U11.4 (V_{DD}), U12.4 (V_{DD}), U13.4 (V_{DD}), U14.4 (V_{DD}), U15.4 (V_{DD}), U16.4 (V_{DD}), U17.4 (V_{DD}), U18.4 (V_{DD}), U19.4 (V_{DD}), U20.4 (V_{DD}), U21.4 (V_{DD}), U22.4 (V_{DD}), U23.4 (V_{DD}), U24.4 (V_{DD}), U25.4 (V_{DD}), U26.4 (V_{DD}), U27.4 (V_{DD}), U28.4 (V_{DD}), U29.4 (V_{DD}), U30.4 (V_{DD}), U31.4 (V_{DD}), U32.4 (V_{DD}), U33.4 (V_{DD}), U34.4 (V_{DD}), U35.4 (V_{DD}), U36.4 (V_{DD})
/A0: U2.15 (A0), U3.11 (PA5), U4.15 (A0)
/A1: U2.16 (A1), U3.12 (PA6), U4.16 (A1)
/A2: U2.17 (A2), U3.13 (PA7), U4.17 (A2)
/A3: U2.18 (A3), U3.18 (PA8), U4.18 (A3)
/A4: U2.19 (A4), U3.16 (PB2), U4.19 (A4)
/CS_DRIVE: U3.14 (PB0), U4.20 (~CS)
/CS_TEMP: U2.20 (~CS), U3.15 (PB1)
/DAC: R7.2, U3.10 (PA4)
/EN: U2.22 (~EN), U3.9 (PA3), U4.22 (~EN)
/G1: C1.2, Q1.1 (G), U4.12 (S1)
/G2: C2.2, Q2.1 (G), U4.11 (S2)
/G3: C3.2, Q3.1 (G), U4.10 (S3)
/G4: C4.2, Q4.1 (G), U4.9 (S4)
/G5: C5.2, Q5.1 (G), U4.8 (S5)
/G6: C6.2, Q6.1 (G), U4.7 (S6)
/G7: C7.2, Q7.1 (G), U4.6 (S7)
/G8: C8.2, Q8.1 (G), U4.5 (S8)
/G9: C9.2, Q9.1 (G), U4.4 (S9)
/G10: C10.2, Q10.1 (G), U4.3 (S10)
/G11: C11.2, Q11.1 (G), U4.2 (S11)
/G12: C12.2, Q12.1 (G), U4.1 (S12)
/G13: C13.2, Q13.1 (G), U4.48 (S13)
/G14: C14.2, Q14.1 (G), U4.47 (S14)
/G15: C16.2, Q16.1 (G), U4.46 (S15)
/G16: C15.2, Q15.1 (G), U4.45 (S16)
/G17: C24.2, Q24.1 (G), U4.25 (S17)
/G18: C23.2, Q23.1 (G), U4.26 (S18)
/G19: C19.2, Q19.1 (G), U4.27 (S19)
/G20: C20.2, Q20.1 (G), U4.28 (S20)
/G21: C22.2, Q22.1 (G), U4.29 (S21)
/G22: C21.2, Q21.1 (G), U4.30 (S22)
/G23: C18.2, Q18.1 (G), U4.31 (S23)
/G24: C17.2, Q17.1 (G), U4.32 (S24)
/G25: C31.2, Q31.1 (G), U4.33 (S25)
/G26: C32.2, Q32.1 (G), U4.34 (S26)
/G27: C27.2, Q27.1 (G), U4.35 (S27)
/G28: C28.2, Q28.1 (G), U4.36 (S28)
/G29: C26.2, Q26.1 (G), U4.37 (S29)
/G30: C25.2, Q25.1 (G), U4.38 (S30)
/G31: C30.2, Q30.1 (G), U4.39 (S31)
/G32: C29.2, Q29.1 (G), U4.40 (S32)
/RX: J2.3, U3.20 (PA10)
/RX2: J4.13, U3.25 (PA15)
/SWCLK: J4.6, U3.24 (PA14)
/SWDIO: J4.4, U3.23 (PA13)
/TEMP: R1.2, U1.7, U3.6 (PA0)
/TH1: U2.10 (S3), U5.3 (V_{OUT})
/TH2: U2.9 (S4), U6.3 (V_{OUT})
/TH3: U2.8 (S5), U7.3 (V_{OUT})
/TH4: U2.7 (S6), U8.3 (V_{OUT})
/TH5: U2.6 (S7), U9.3 (V_{OUT})
/TH6: U2.5 (S8), U10.3 (V_{OUT})
/TH7: U2.4 (S9), U11.3 (V_{OUT})
/TH8: U2.3 (S10), U12.3 (V_{OUT})
/TH9: U2.2 (S11), U13.3 (V_{OUT})
/TH10: U2.1 (S12), U14.3 (V_{OUT})
/TH11: U2.48 (S13), U15.3 (V_{OUT})
/TH12: U2.47 (S14), U16.3 (V_{OUT})
/TH13: U2.46 (S15), U17.3 (V_{OUT})
/TH14: U2.45 (S16), U18.3 (V_{OUT})
/TH15: U2.25 (S17), U20.3 (V_{OUT})
/TH16: U2.26 (S18), U19.3 (V_{OUT})
/TH17: U2.27 (S19), U28.3 (V_{OUT})
/TH18: U2.28 (S20), U27.3 (V_{OUT})
/TH19: U2.29 (S21), U23.3 (V_{OUT})
/TH20: U2.30 (S22), U24.3 (V_{OUT})
/TH21: U2.31 (S23), U26.3 (V_{OUT})
/TH22: U2.32 (S24), U25.3 (V_{OUT})
/TH23: U2.33 (S25), U22.3 (V_{OUT})
/TH24: U2.34 (S26), U21.3 (V_{OUT})
/TH25: U2.35 (S27), U35.3 (V_{OUT})
/TH26: U2.36 (S28), U36.3 (V_{OUT})
/TH27: U2.37 (S29), U31.3 (V_{OUT})
/TH28: U2.38 (S30), U32.3 (V_{OUT})
/TH29: U2.39 (S31), U30.3 (V_{OUT})
/TH30: U2.40 (S32), U29.3 (V_{OUT})
/TH31: U2.12 (S1), U34.3 (V_{OUT})
/TH32: U2.11 (S2), U33.3 (V_{OUT})
/TX: J2.2, U3.19 (PA9)
/TX2: J4.14, U3.8 (PA2)
/USB_DM: J3.2 (D-), U3.21 (PA11)
/USB_DP: J3.3 (D+), U3.22 (PA12)
/WR: U2.21 (~WR), U3.7 (PA1), U4.21 (~WR)
/~RST: J4.12, U3.4 (NRST)
GND: C1.1, C2.1, C3.1, C4.1, C5.1, C6.1, C7.1, C8.1, C9.1, C10.1, C11.1, C12.1, C13.1, C14.1, C15.1, C16.1, C17.1, C18.1, C19.1, C20.1, C21.1, C22.1, C23.1, C24.1, C25.1, C26.1, C27.1, C28.1, C29.1, C30.1, C31.1, C32.1, C33.1, C34.1, C35.2, C36.2, C37.2, C38.1, J1.2, J2.4, J3.5 (GND), J3.6 (Shield), J4.5, J4.7, Q1.2 (S), Q2.2 (S), Q3.2 (S), Q4.2 (S), Q5.2 (S), Q6.2 (S), Q7.2 (S), Q8.2 (S), Q9.2 (S), Q10.2 (S), Q11.2 (S), Q12.2 (S), Q13.2 (S), Q14.2 (S), Q15.2 (S), Q16.2 (S), Q17.2 (S), Q18.2 (S), Q19.2 (S), Q20.2 (S), Q21.2 (S), Q22.2 (S), Q23.2 (S), Q24.2 (S), Q25.2 (S), Q26.2 (S), Q27.2 (S), Q28.2 (S), Q29.2 (S), Q30.2 (S), Q31.2 (S), Q32.2 (S), R2.1, R5.1, R6.1, R9.1, U1.4 (V-), U1.9 (V-), U2.23 (GND), U2.24 (VSS), U3.31 (BOOT0), U3.33 (VSS), U4.23 (GND), U4.24 (VSS), U5.2 (GND), U6.2 (GND), U7.2 (GND), U8.2 (GND), U9.2 (GND), U10.2 (GND), U11.2 (GND), U12.2 (GND), U13.2 (GND), U14.2 (GND), U15.2 (GND), U16.2 (GND), U17.2 (GND), U18.2 (GND), U19.2 (GND), U20.2 (GND), U21.2 (GND), U22.2 (GND), U23.2 (GND), U24.2 (GND), U25.2 (GND), U26.2 (GND), U27.2 (GND), U28.2 (GND), U29.2 (GND), U30.2 (GND), U31.2 (GND), U32.2 (GND), U33.2 (GND), U34.2 (GND), U35.2 (GND), U36.2 (GND), Y1.2, Y1.4
unnamed: D1.2 (A), U3.28 (PB5)
unnamed: D1.1 (K), R5.2
unnamed: D2.2 (A), U3.29 (PB6)
unnamed: D2.1 (K), R6.2
unnamed: R2.2, R3.1, R4.2
unnamed: R7.1, R8.1, R9.2, U1.3 (+)
unnamed: R10.1, U1.1, U1.2 (-)
unnamed: U1.5 (+), U2.43 (D)
unnamed: R1.1, R3.2, U1.6 (-)
unnamed: C34.2, U3.2 (PC14), Y1.1
unnamed: C33.2, U3.3 (PC15), Y1.3
unnamed: R10.2, U4.43 (D)

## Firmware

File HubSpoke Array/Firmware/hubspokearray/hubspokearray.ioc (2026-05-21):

#MicroXplorer Configuration settings - do not modify
ADC.ClockPrescaler=ADC_CLOCK_ASYNC_DIV32
ADC.IPParameters=SamplingTime,ClockPrescaler
ADC.SamplingTime=ADC_SAMPLETIME_12CYCLES_5
CAD.formats=
CAD.pinconfig=
CAD.provider=
File.Version=6
GPIO.groupedBy=Group By Peripherals
KeepUserPlacement=false
Mcu.CPN=STM32L052K8U6
Mcu.Family=STM32L0
Mcu.IP0=ADC
Mcu.IP1=NVIC
Mcu.IP2=RCC
Mcu.IP3=SYS
Mcu.IP4=USART1
Mcu.IP5=USART2
Mcu.IPNb=6
Mcu.Name=STM32L052K(6-8)Ux
Mcu.Package=UFQFPN32
Mcu.Pin0=PA0
Mcu.Pin1=PA1
Mcu.Pin10=PB2
Mcu.Pin11=PA8
Mcu.Pin12=PA9
Mcu.Pin13=PA10
Mcu.Pin14=PA15
Mcu.Pin15=PB5
Mcu.Pin16=PB6
Mcu.Pin17=VP_SYS_VS_Systick
Mcu.Pin2=PA2
Mcu.Pin3=PA3
Mcu.Pin4=PA4
Mcu.Pin5=PA5
Mcu.Pin6=PA6
Mcu.Pin7=PA7
Mcu.Pin8=PB0
Mcu.Pin9=PB1
Mcu.PinsNb=18
Mcu.ThirdPartyNb=0
Mcu.UserConstants=
Mcu.UserName=STM32L052K8Ux
MxCube.Version=6.14.0
MxDb.Version=DB.6.0.140
NVIC.ForceEnableDMAVector=true
NVIC.HardFault_IRQn=true\:0\:0\:false\:false\:true\:false\:false\:false
NVIC.NonMaskableInt_IRQn=true\:0\:0\:false\:false\:true\:false\:false\:false
NVIC.PendSV_IRQn=true\:0\:0\:false\:false\:true\:false\:false\:false
NVIC.SVC_IRQn=true\:0\:0\:false\:false\:true\:false\:false\:true
NVIC.SysTick_IRQn=true\:3\:0\:false\:false\:true\:false\:true\:false
NVIC.USART1_IRQn=true\:0\:0\:false\:false\:true\:true\:true\:true
NVIC.USART2_IRQn=true\:0\:0\:false\:false\:true\:true\:true\:true
PA0.Locked=true
PA0.Mode=IN0
PA0.Signal=ADC_IN0
PA1.GPIOParameters=GPIO_Label
PA1.GPIO_Label=WR
PA1.Locked=true
PA1.Signal=GPIO_Output
PA10.Mode=Asynchronous
PA10.Signal=USART1_RX
PA15.Locked=true
PA15.Mode=Asynchronous
PA15.Signal=USART2_RX
PA2.Mode=Asynchronous
PA2.Signal=USART2_TX
PA3.GPIOParameters=GPIO_Label
PA3.GPIO_Label=EN
PA3.Locked=true
PA3.Signal=GPIO_Output
PA4.GPIOParameters=GPIO_Label
PA4.GPIO_Label=DAC
PA4.Locked=true
PA4.Signal=GPIO_Output
PA5.GPIOParameters=GPIO_Label
PA5.GPIO_Label=A0
PA5.Locked=true
PA5.Signal=GPIO_Output
PA6.GPIOParameters=GPIO_Label
PA6.GPIO_Label=A1
PA6.Locked=true
PA6.Signal=GPIO_Output
PA7.GPIOParameters=GPIO_Label
PA7.GPIO_Label=A2
PA7.Locked=true
PA7.Signal=GPIO_Output
PA8.GPIOParameters=GPIO_Label
PA8.GPIO_Label=A3
PA8.Locked=true
PA8.Signal=GPIO_Output
PA9.Locked=true
PA9.Mode=Asynchronous
PA9.Signal=USART1_TX
PB0.GPIOParameters=GPIO_Label
PB0.GPIO_Label=CS_DRIVE
PB0.Locked=true
PB0.Signal=GPIO_Output
PB1.GPIOParameters=GPIO_Label
PB1.GPIO_Label=CS_TEMP
PB1.Locked=true
PB1.Signal=GPIO_Output
PB2.GPIOParameters=GPIO_Label
PB2.GPIO_Label=A4
PB2.Locked=true
PB2.Signal=GPIO_Output
PB5.GPIOParameters=GPIO_Label
PB5.GPIO_Label=LD1
PB5.Locked=true
PB5.Signal=GPIO_Output
PB6.GPIOParameters=GPIO_Label
PB6.GPIO_Label=LD2
PB6.Locked=true
PB6.Signal=GPIO_Output
PinOutPanel.RotationAngle=0
ProjectManager.AskForMigrate=true
ProjectManager.BackupPrevious=false
ProjectManager.CompilerLinker=GCC
ProjectManager.CompilerOptimize=6
ProjectManager.ComputerToolchain=false
ProjectManager.CoupleFile=false
ProjectManager.CustomerFirmwarePackage=
ProjectManager.DefaultFWLocation=true
ProjectManager.DeletePrevious=true
ProjectManager.DeviceId=STM32L052K8Ux
ProjectManager.FirmwarePackage=STM32Cube FW_L0 V1.12.3
ProjectManager.FreePins=false
ProjectManager.HalAssertFull=false
ProjectManager.HeapSize=0x200
ProjectManager.KeepUserCode=true
ProjectManager.LastFirmware=true
ProjectManager.LibraryCopy=1
ProjectManager.MainLocation=Core/Src
ProjectManager.NoMain=false
ProjectManager.PreviousToolchain=
ProjectManager.ProjectBuild=false
ProjectManager.ProjectFileName=hubspokearray.ioc
ProjectManager.ProjectName=hubspokearray
ProjectManager.ProjectStructure=
ProjectManager.RegisterCallBack=
ProjectManager.StackSize=0x400
ProjectManager.TargetToolchain=STM32CubeIDE
ProjectManager.ToolChainLocation=
ProjectManager.UAScriptAfterPath=
ProjectManager.UAScriptBeforePath=
ProjectManager.UnderRoot=true
ProjectManager.functionlistsort=1-SystemClock_Config-RCC-false-HAL-false,2-MX_GPIO_Init-GPIO-false-HAL-true,3-MX_ADC_Init-ADC-false-HAL-true,4-MX_USART1_UART_Init-USART1-false-HAL-true,5-MX_USART2_UART_Init-USART2-false-HAL-true,6-MX_USB_DEVICE_Init-USB_DEVICE-false-HAL-false
RCC.48CLKFreq_Value=24000000
RCC.48RNGFreq_Value=48000000
RCC.48USBFreq_Value=48000000
RCC.AHBFreq_Value=16000000
RCC.APB1Freq_Value=16000000
RCC.APB1TimFreq_Value=16000000
RCC.APB2Freq_Value=16000000
RCC.APB2TimFreq_Value=16000000
RCC.FCLKCortexFreq_Value=16000000
RCC.FamilyName=M
RCC.HCLKFreq_Value=16000000
RCC.HSI16_VALUE=16000000
RCC.HSI48MClockSelection=RCC_USBCLKSOURCE_HSI48
RCC.HSI48_VALUE=48000000
RCC.HSI_VALUE=16000000
RCC.I2C1Freq_Value=16000000
RCC.IPParameters=48CLKFreq_Value,48RNGFreq_Value,48USBFreq_Value,AHBFreq_Value,APB1Freq_Value,APB1TimFreq_Value,APB2Freq_Value,APB2TimFreq_Value,FCLKCortexFreq_Value,FamilyName,HCLKFreq_Value,HSI16_VALUE,HSI48MClockSelection,HSI48_VALUE,HSI_VALUE,I2C1Freq_Value,LPTIMFreq_Value,LSE_VALUE,LSI_VALUE,MCOPinFreq_Value,MSI_VALUE,PLLCLKFreq_Value,RTCFreq_Value,SYSCLKFreq_VALUE,SYSCLKSource,TIMFreq_Value,TimerFreq_Value,USART1Freq_Value,USART2Freq_Value,VCOOutputFreq_Value,WatchDogFreq_Value
RCC.LPTIMFreq_Value=16000000
RCC.LSE_VALUE=32768
RCC.LSI_VALUE=37000
RCC.MCOPinFreq_Value=16000000
RCC.MSI_VALUE=2097000
RCC.PLLCLKFreq_Value=24000000
RCC.RTCFreq_Value=37000
RCC.SYSCLKFreq_VALUE=16000000
RCC.SYSCLKSource=RCC_SYSCLKSOURCE_HSI
RCC.TIMFreq_Value=16000000
RCC.TimerFreq_Value=16000000
RCC.USART1Freq_Value=16000000
RCC.USART2Freq_Value=16000000
RCC.VCOOutputFreq_Value=48000000
RCC.WatchDogFreq_Value=37000
USART1.IPParameters=VirtualMode-Asynchronous
USART1.VirtualMode-Asynchronous=VM_ASYNC
USART2.IPParameters=VirtualMode-Asynchronous
USART2.VirtualMode-Asynchronous=VM_ASYNC
VP_SYS_VS_Systick.Mode=SysTick
VP_SYS_VS_Systick.Signal=SYS_VS_Systick
board=custom
isbadioc=false

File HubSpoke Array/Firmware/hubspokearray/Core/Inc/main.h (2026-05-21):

/* USER CODE BEGIN Header */
/**
  ******************************************************************************
  * @file           : main.h
  * @brief          : Header for main.c file.
  *                   This file contains the common defines of the application.
  ******************************************************************************
  * @attention
  *
  * Copyright (c) 2025 STMicroelectronics.
  * All rights reserved.
  *
  * This software is licensed under terms that can be found in the LICENSE file
  * in the root directory of this software component.
  * If no LICENSE file comes with this software, it is provided AS-IS.
  *
  ******************************************************************************
  */
/* USER CODE END Header */

/* Define to prevent recursive inclusion -------------------------------------*/
#ifndef __MAIN_H
#define __MAIN_H

#ifdef __cplusplus
extern "C" {
#endif

/* Includes ------------------------------------------------------------------*/
#include "stm32l0xx_hal.h"

/* Private includes ----------------------------------------------------------*/
/* USER CODE BEGIN Includes */

/* USER CODE END Includes */

/* Exported types ------------------------------------------------------------*/
/* USER CODE BEGIN ET */

/* USER CODE END ET */

/* Exported constants --------------------------------------------------------*/
/* USER CODE BEGIN EC */

/* USER CODE END EC */

/* Exported macro ------------------------------------------------------------*/
/* USER CODE BEGIN EM */

/* USER CODE END EM */

/* Exported functions prototypes ---------------------------------------------*/
void Error_Handler(void);

/* USER CODE BEGIN EFP */
void DEBUG_PRINT(char * format, ...);
void printtemps(uint32_t * temps);
/* USER CODE END EFP */

/* Private defines -----------------------------------------------------------*/
#define WR_Pin GPIO_PIN_1
#define WR_GPIO_Port GPIOA
#define EN_Pin GPIO_PIN_3
#define EN_GPIO_Port GPIOA
#define DAC_Pin GPIO_PIN_4
#define DAC_GPIO_Port GPIOA
#define A0_Pin GPIO_PIN_5
#define A0_GPIO_Port GPIOA
#define A1_Pin GPIO_PIN_6
#define A1_GPIO_Port GPIOA
#define A2_Pin GPIO_PIN_7
#define A2_GPIO_Port GPIOA
#define CS_DRIVE_Pin GPIO_PIN_0
#define CS_DRIVE_GPIO_Port GPIOB
#define CS_TEMP_Pin GPIO_PIN_1
#define CS_TEMP_GPIO_Port GPIOB
#define A4_Pin GPIO_PIN_2
#define A4_GPIO_Port GPIOB
#define A3_Pin GPIO_PIN_8
#define A3_GPIO_Port GPIOA
#define LD1_Pin GPIO_PIN_5
#define LD1_GPIO_Port GPIOB
#define LD2_Pin GPIO_PIN_6
#define LD2_GPIO_Port GPIOB

/* USER CODE BEGIN Private defines */

//#define MAIN_BOARD

#define HEATER_RETENTION 100

/* USER CODE END Private defines */

#ifdef __cplusplus
}
#endif

#endif /* __MAIN_H */

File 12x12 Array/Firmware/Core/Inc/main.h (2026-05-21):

/* USER CODE BEGIN Header */
/**
  ******************************************************************************
  * @file           : main.h
  * @brief          : Header for main.c file.
  *                   This file contains the common defines of the application.
  ******************************************************************************
  * @attention
  *
  * Copyright (c) 2025 STMicroelectronics.
  * All rights reserved.
  *
  * This software is licensed under terms that can be found in the LICENSE file
  * in the root directory of this software component.
  * If no LICENSE file comes with this software, it is provided AS-IS.
  *
  ******************************************************************************
  */
/* USER CODE END Header */

/* Define to prevent recursive inclusion -------------------------------------*/
#ifndef __MAIN_H
#define __MAIN_H

#ifdef __cplusplus
extern "C" {
#endif

/* Includes ------------------------------------------------------------------*/
#include "stm32f1xx_hal.h"

/* Private includes ----------------------------------------------------------*/
/* USER CODE BEGIN Includes */

/* USER CODE END Includes */

/* Exported types ------------------------------------------------------------*/
/* USER CODE BEGIN ET */

/* USER CODE END ET */

/* Exported constants --------------------------------------------------------*/
/* USER CODE BEGIN EC */

/* USER CODE END EC */

/* Exported macro ------------------------------------------------------------*/
/* USER CODE BEGIN EM */

/* USER CODE END EM */

void HAL_TIM_MspPostInit(TIM_HandleTypeDef *htim);

/* Exported functions prototypes ---------------------------------------------*/
void Error_Handler(void);

/* USER CODE BEGIN EFP */

/* USER CODE END EFP */

/* Private defines -----------------------------------------------------------*/
#define LED1_Pin GPIO_PIN_3
#define LED1_GPIO_Port GPIOE
#define LED2_Pin GPIO_PIN_4
#define LED2_GPIO_Port GPIOE
#define VG9_Pin GPIO_PIN_8
#define VG9_GPIO_Port GPIOD
#define VG10_Pin GPIO_PIN_9
#define VG10_GPIO_Port GPIOD
#define VG11_Pin GPIO_PIN_10
#define VG11_GPIO_Port GPIOD
#define VG12_Pin GPIO_PIN_11
#define VG12_GPIO_Port GPIOD
#define TEMP_SEL_Pin GPIO_PIN_11
#define TEMP_SEL_GPIO_Port GPIOC
#define VG1_Pin GPIO_PIN_0
#define VG1_GPIO_Port GPIOD
#define VG2_Pin GPIO_PIN_1
#define VG2_GPIO_Port GPIOD
#define VG3_Pin GPIO_PIN_2
#define VG3_GPIO_Port GPIOD
#define VG4_Pin GPIO_PIN_3
#define VG4_GPIO_Port GPIOD
#define VG5_Pin GPIO_PIN_4
#define VG5_GPIO_Port GPIOD
#define VG6_Pin GPIO_PIN_5
#define VG6_GPIO_Port GPIOD
#define VG7_Pin GPIO_PIN_6
#define VG7_GPIO_Port GPIOD
#define VG8_Pin GPIO_PIN_7
#define VG8_GPIO_Port GPIOD

/* USER CODE BEGIN Private defines */

/* USER CODE END Private defines */

#ifdef __cplusplus
}
#endif

#endif /* __MAIN_H */

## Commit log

2026-05-26 Start flow shims
    [element.kicad_sch, heater.kicad_pcb, heater.kicad_sch, heater.step]
2026-05-26 TS25 PCBs fit in CAD
    [heater.kicad_pcb, heater.step, temp_sensor.step, temp_sensors.kicad_pcb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]
2026-05-26 Controller DRC/ERC clean
    [controller.kicad_pcb, controller.kicad_sch, controller.step, psu.kicad_sch]
2026-05-27 Add 17 element versions
    [controller.kicad_pcb, element.kicad_sch, heater.kicad_pcb, heater.kicad_sch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]
2026-05-27 All boards DRC/ERC clean
    [controller.kicad_pcb, controller.kicad_sch, element.kicad_sch, heater.kicad_pcb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]
